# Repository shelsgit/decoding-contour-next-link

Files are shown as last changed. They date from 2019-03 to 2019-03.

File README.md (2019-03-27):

# ContourNextLink2.4/600PumpSeries - Display and Low Alarm
Instructions to make a display of your current blood sugar level with a Low Alarm and Snooze Button (for use with a Contour Next Link 2.4 and 600 series pump)<br/><br/>
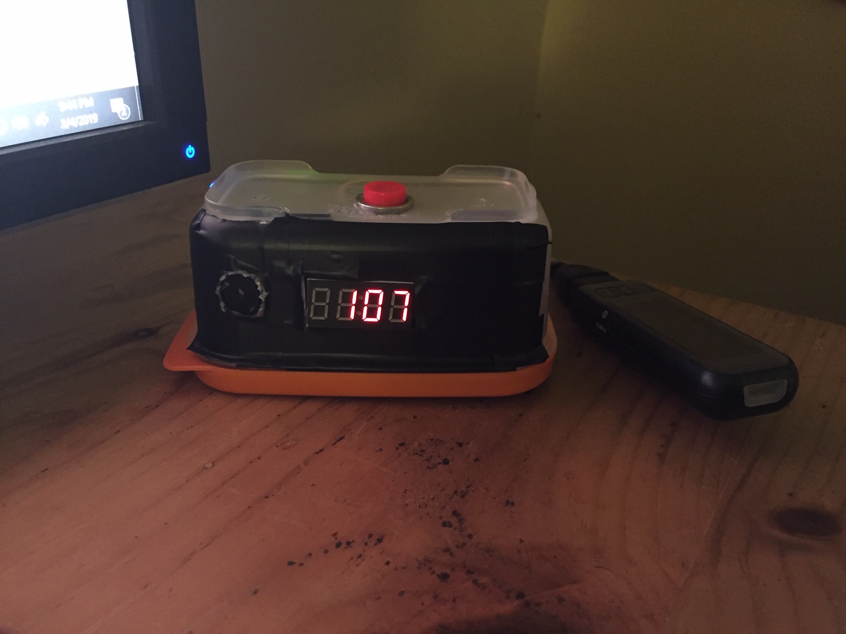
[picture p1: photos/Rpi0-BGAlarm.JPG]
BGAlarm

## Disclaimer And Warning
* All information, thought, and code described here is intended for informational and educational purposes only.<br/>
* Make/use at your own risk, and do not use the information or code to make medical decisions.<br/>
* Use of code from github.com is without warranty or formal support of any kind. Please review this repository’s LICENSE for details.<br/>
* All product and company names, trademarks, servicemarks, registered trademarks, and registered servicemarks are the property of their respective holders. Their use is for information purposes and does not imply any affiliation with or endorsement by them.<br/>
* This project has no association with and is not endorsed by Medtronic, or any other company.<br/>

## Components/Requirements
* Raspberry Pi Zero WF (RPi0)- for wifi and headless install/no miniHDMI converter needed (https://www.adafruit.com/product/3708) 
* SD/MicroSD Card (https://www.adafruit.com/product/1294)
* TM 1637 Display (https://www.amazon.com/gp/product/B01DKISMXK/ref=ppx_yo_dt_b_asin_title_o07_s00?ie=UTF8&psc=1)
* Pushbutton (https://www.amazon.com/gp/product/B01C8CS7EI/ref=ppx_yo_dt_b_asin_title_o00_s00?ie=UTF8&psc=1)
* Piezo Buzzer (https://www.adafruit.com/product/160?gclid=EAIaIQobChMIo-L8trDn4AIVyIWzCh3VjwtYEAQYASABEgKqyPD_BwE)
* Contour Next Link 2.4 (CNL) and Medtronic 600 Series Pump
* OTG cable to connect CNL to RPi0(https://www.adafruit.com/product/1099)
* Wires to connect PB and Display to RPi0 (https://www.adafruit.com/product/1950)

## RPi0 - Configure, Install Software, Start it on bootup as Service
1. Install Raspbian Lite onto your SD Card (you don't need to format or partition it prior/the install will do it):
	* Download Raspian Lite: https://www.raspberrypi.org/downloads/raspbian/
    - Note: I used 2018-10-09-raspbian-stretch (I could not headlessly configure the wireless with the later version/ not sure why - 2018-11-13-raspbian-stretch-lite)
	* Get/install Etcher (to use to move/install Raspian onto the SD card): https://www.balena.io/etcher/
	* Open etcher and flash Raspian Lite onto your SD card (Note: You don't need to format it beforehand - it will and will create a small 'boot' drive and another drive)
2. On your SD card - Edit the files below (refer to: https://learn.adafruit.com/raspberry-pi-zero-creation/text-file-editing)
	* Open file: config.txt (DONT USE NOTEPAD, Use Notepad++ or an app that won't mess up formatting):
		* At bottom add:	
		```
		# Enable UART
		enable_uart=1
		```
	* Create new file called: wpa_supplicant.conf
		* Open/edit it with your info/example below (left alligned):
		```
		ctrl_interface=DIR=/var/run/wpa_supplicant GROUP=netdev
		update_config=1
		country=US
		 
		network={
			 ssid="YOURSSID"
			 psk="YOURPASSWORD"
			 scan_ssid=1
		}
		```
	* Create a new file called ssh (no .txt extention or any extension), and don't edit it/keep it as an empty file.
3. Move the SD to the RPi0, and confirm it connects to your wireless network:
	* Eject your SD card and put it into your RPi0.  Use the 1st/TOPMOST USB PORT (if using a RPi0) and plug it into your computer - wait until green light stops blinking.
	* If you are using Windows, install Bonjour Print Services for Windows v2.0.2 - https://support.apple.com/kb/DL999?locale=en_US (I'm not sure if this is actually required but I did it)
	* Open a command prompt and try to ping the RPi0 by hostname - With windows prompt: ping raspberrypi.local
	* If you can't ping it, then you'll need to ping it by IP instead.  To figure out the RPi0's IP I have my home firewall send its event logging to: https://papertrailapp.com/.  You can setup the Rpi0 to do this as well for remote debugging, if you want.
4. SSH to the RPi0 (use PuTTY/install if you don't have):
	* Open Putty, and Enter hostname: pi@hostname(or IP) (all others default/SSH)
	* Enter default RPi0 password: raspberry
5. RPi0 Initial Setup (refer to: https://learn.adafruit.com/raspberry-pi-zero-creation/first-login)
	* Run system update:
	```
    > sudo apt-get update
    > sudo apt-get upgrade
	```
	* Run:
  	```
    > sudo raspi-config
	```
	* Select/do:
		* 'Change user password'(or similar) - change your password from default (remember it/don't loose it!)
		* 'Interfacing Options' and choose options to turn on SSH (although maybe not really needed being a boot file was made to set this on already)
		* 'Advanced Options' - Choose A1-Expand Filesystem (so that all of you SD card is available)
		* 'Update this Tool to the latest Version'

6. Install additional required Rpi0 software:
	* Confirm that you have Python 2.7 and PIP installed (Raspbian Stretch Lite comes w Python 2 and PIP for python2):
  	 ```
    > python --version
    > pip --version
	 ```
	* Install needed libraries:
	 ```
    > sudo apt-get install libusb-1.0-0-dev
    > sudo apt-get install libudev-dev
    > sudo apt-get install python-lzo
    > sudo sudo apt-get install git-core
	 ```
	* Install needed python packages:
  	 ```
    > sudo -H pip2 install cython
    > sudo -H pip2 install hidapi
    > sudo -H pip2 install requests astm PyCrypto crc16 python-dateutil
    > sudo -H pip2 install RPi.GPIO (was actually already installed)
	 ```
    - Note: If you get an error when trying any of the above installs, then read the error you get, to see which .h file or director was missing and search for a package which may include it with: apt-cache search FILENAME.  Then install it with: sudo apt-get install PACKAGENAME  
7. Git - Clone and switch to branch:
	* Clone git project:
  	 ```
    > git clone https://github.com/shelsgit/decoding-contour-next-link.git
	 ```
	* Switch to Alarm Clock Branch:
  	 ```
    > git checkout CNL-RPi0-AlarmClock
	 ```
8. Create a service to run the python clock module, at bootup:<br/>
   ** Make sure that by this step you've wired the Pushbutton and Display to the RPi0 (as in the 'Wiring' section below)  
	* Move the CNLdisplay.service file, as root to the system folder below, and then tell systemd to look for the new service:
  	 ```
    > cd /home/pi/decoding-contour-next-link/
	> sudo cp CNLdisplay.service /etc/systemd/system/CNLdisplay.service
	> sudo systemctl daemon-reload
  	 ```
	* Test it: try to start the service:
  	 ```
	> sudo systemctl start CNLdisplay.service
  	 ```
	* Check your service, to make sure its running OK:
  	 ```	
	> systemctl status CNLdisplay 
  	 ```	
	* Test it: Stop the service (and you should see 'err' on your display):
  	 ```
	> sudo systemctl stop CNLdisplay.service
	```
	* When you the service works, make it run automatically from boot up:
	```
	> sudo systemctl enable CNLdisplay.service
	```
9. Make a backup of your SD Card (optional)
	* This site looks like it has good backup/restore directions: https://www.howtogeek.com/341944/how-to-clone-your-raspberry-pi-sd-card-for-foolproof-backup/
	
## Wiring
* TM1637 Display -> RPi0 (fyi, the GPIO pin layout for a RPi0 is the same as a RPi2 or RPi3 with 40pins):
	* CLK -> GPIO23 (Pin 16, 8th pin down on right side)(top of RPi0 is when the GPIO pins are on the right)
	* DiO -> GPIO24 (Pin 18, 9th pin down on right side)
	* V -> Pi 5V Pin (Pin 2, Top pin on right side)(Could use 3V/Pin1(top,left) instead/less bright)
	* Grnd -> Pi Grnd Pin (Pin 20, 10th down on right side)
* Peizo Buzzer -> RPi0:
	* '+'-> GPIO17 (Pin 11, 6th pin down on left side)
	* Grnd -> Pi Ground Pin (Pin 9, 5th down on left side)
* Wiring Snooze Push Button -> RPi0:
	* either pushbutton terminal -> GPIO26 (left, 2nd from bottom pin)(grnd is bottom left pin)
	* other pushbutton terminal -> grnd (bottom left pin)
* Power(microUSB cable) -> RPi0:
	* microUSB -> TOP RPi0 microUSB port
* OTG cable -> RPi0:
	* OTG Cable -> 2nd (not TOP) RPi0 microUSB port

## Notes
* The Display's 1st(leftmost) digit is to display status:
	* There is a continual blinking underscore, as a heartbeat, to show that the program is running/hasn't crashed
		* The program has been very reliable for me, but if the program does crash, the display will now show 'OFF' for 20sec, then go blank, and the Rpi will be powered off.
		* If the blinking heartbeat stops for ~10s this is normal and indicates when the CNL is attempting to read from the pump (and CNL will blink yellow)
	* The 1st digit will also indicate any Recently missed, or Stale Data:
		* 0 -  the RPi0 missed one reading from the CNL (this will happen occasionally)
		* 8 - the RPi0 missed more than one reading
		* 8888 - the display data should be considered 'stale', it is ~>17min old
* The low BG setpoint = <70, and snooze time is 20min (you can change this by editing 'read_minimed_next24.py' setpoint variables near the top of the script)  
* When you turn the RPi0 on, it will take ~30sec to get your first reading (in order to give the RPi0 and meter time to startup).
* When you turn the RPi0 on, the script will run as a service, AND IT WILL STOP AND POWEROFF THE RPi0 AFTER 9 hours (this is because I want it to shutdown properly rather than pulling the power each morning, and don't want to have to SSH in each day to properly shut it down)(If you want it powered on longer or always instead, edit (then reload) your /etc/systemd/system/CNLdisplay.service)
* When the pump is calibrating or a calibration is required - the display will show 'CAL'
* The display will show 'LO' and 'HI' when the pump does.  If your display shows a value such as 776, this means something such as 'sensor updating', for example (refer to your pump, as the display will just show the big number).
* When the pump shows no signal - the display will show old then stale indication as described above (so that you can still see your previous BG and see that it is getting old and eventually stale)
* If the snooze is active and you unplug the CNL, it will buzz again when the snooze time is up until the next CNL check (when BG is not low or the data gets stale/display=8888)

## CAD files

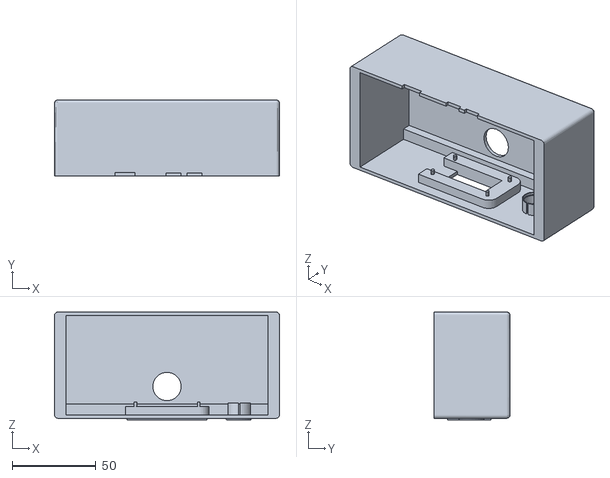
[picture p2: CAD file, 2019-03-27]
3D_Case/RPi0ClockCase1-TOP.stl
134.5 x 45.5 x 64.5

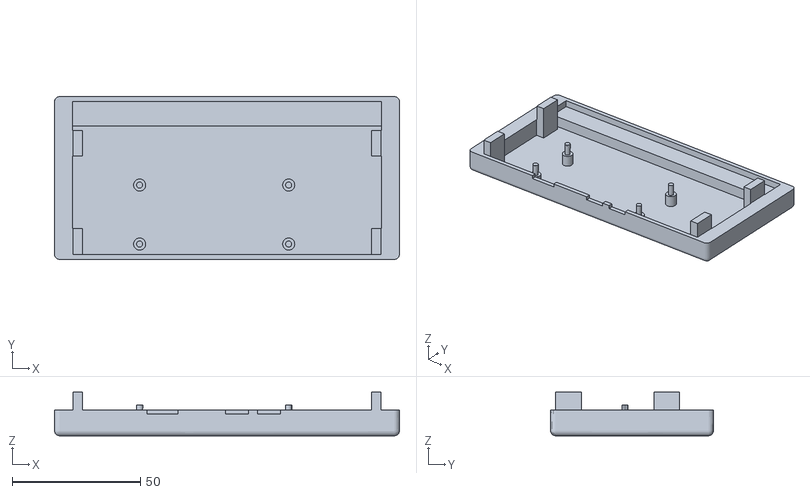
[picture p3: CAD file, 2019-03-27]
3D_Case/RPi0ClockCase1-BOTTOM.stl
134.5 x 63.5 x 17.0

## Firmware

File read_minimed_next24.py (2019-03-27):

#!/usr/bin/env python

import logging
from logging.handlers import RotatingFileHandler # Added to limit log file size
# logging.basicConfig has to be before astm import, otherwise logs don't appear
# Logging - filemode=w overrights logfile each time script is ran, .DEBUG, shows all info,warning and debug logs, .WARNING shows warning + higher, .ERROR error+)
logging.basicConfig(filename='read_mini.log',filemode='w',format='%(asctime)s %(levelname)s [%(name)s] %(message)s',level=logging.WARNING)
# a workaround on missing hidapi.dll on my windows (allows testing from saved files, but not download of pump)
try:
    import hid # pip install hidapi - Platform independant
except WindowsError:
    pass
import astm # pip install astm
import struct
import binascii
import datetime
import time
from time import sleep
import crc16 # pip install crc16
import Crypto.Cipher.AES # pip install PyCrypto
import sqlite3
import hashlib
import re
import pickle # needed for local history export
import lzo # pip install python-lzo
# from .pump_history_parser import NGPHistoryEvent, BloodGlucoseReadingEvent
from .helpers import DateTimeHelper
import tm1637 #from github-timwaizenegger/raspberrypi-examples, and copied to working dir
import RPi.GPIO as IO #also imported in tm1637, maybe I can delete from there? (did, testing)

###############################################################
# Wiring: TM1637 Display -> Raspberry Raspberry Pi Zero (RPi0) (fyi, GPIO for RPi0 is same for other RPis(2,3) that have 40pins):
# CLK -> GPIO23 (Pin 16, 8th pin down on right side of RPi0)
# DiO -> GPIO24 (Pin 18, 9th pin down on right side of RPi0)
# V -> Pi 5V Pin (Pin 2, Top pin on right side or RPi0)(Could use 3V/Pin1(top,left) instead/less bright)
# Grnd -> Pi Grnd Pin (Pin 20, 10th down on right side of RPi0)

# Wiring: Buzzer -> Rpi3:
# + -> GPIO17 (Pin 11, 6th pin down on left side of Rpi3)
# Grnd -> Pi Ground Pin (Pin 9, 5th down on right side of Rpi3)

# Wiring Snooze Push Button -> Rpi3:
# A(topleft of button) -> GPIO26 (left, 2nd from bottom pin)(grnd is bottom left pin)
# C(bottomleft of button) -> grnd (bottom left pin or Rpi3)
###############################################################

#SETPOINTS 
BGlowSP = 70 # low alarm/buzzer setpoint (mg/dL)
SnoozeTimeSP = 20 # time to snooze after snooze PB pressed (minutes)

#Define globals
realpumptime = 0
BGLtime = 0
timediff = 0
noCNL = 0
BGL = 777

logger = logging.getLogger(__name__)
handler = RotatingFileHandler("read_mini.log", maxBytes=25000, backupCount=1) # Added to limit log file size
logger.addHandler(handler) # Added to limit log file size

ascii= {
    'ACK' : 0x06,
    'CR' : 0x0D,
    'ENQ' : 0x05,
    'EOT' : 0x04,
    'ETB' : 0x17,
    'ETX' : 0x03,
    'LF' : 0x0A,
    'NAK' : 0x15,
    'STX' : 0x02
}

def ord_hack(char_or_byte):
    return char_or_byte if isinstance(char_or_byte, int) else ord(char_or_byte)

class COM_D_COMMAND:
    HIGH_SPEED_MODE_COMMAND = 0x0412
    TIME_REQUEST = 0x0403
    TIME_RESPONSE = 0x0407
    READ_PUMP_STATUS_REQUEST = 0x0112
    READ_PUMP_STATUS_RESPONSE = 0x013C
    READ_BASAL_PATTERN_REQUEST = 0x0116
    READ_BASAL_PATTERN_RESPONSE = 0x0123
    READ_BOLUS_WIZARD_CARB_RATIOS_REQUEST = 0x012B
    READ_BOLUS_WIZARD_CARB_RATIOS_RESPONSE = 0x012C
    READ_BOLUS_WIZARD_SENSITIVITY_FACTORS_REQUEST = 0x012E
    READ_BOLUS_WIZARD_SENSITIVITY_FACTORS_RESPONSE = 0x012F
    READ_BOLUS_WIZARD_BG_TARGETS_REQUEST = 0x0131
    READ_BOLUS_WIZARD_BG_TARGETS_RESPONSE = 0x0132
    DEVICE_STRING_REQUEST = 0x013A
    DEVICE_STRING_RESPONSE = 0x013B
    DEVICE_CHARACTERISTICS_REQUEST = 0x0200
    DEVICE_CHARACTERISTICS_RESPONSE = 0x0201
    READ_HISTORY_REQUEST = 0x0304
    READ_HISTORY_RESPONSE = 0x0305
    END_HISTORY_TRANSMISSION = 0x030A
    READ_HISTORY_INFO_REQUEST = 0x030C
    READ_HISTORY_INFO_RESPONSE = 0x030D
    UNMERGED_HISTORY_RESPONSE = 0x030E
    INITIATE_MULTIPACKET_TRANSFER = 0xFF00
    MULTIPACKET_SEGMENT_TRANSMISSION = 0xFF01
    MULTIPACKET_RESEND_PACKETS = 0xFF02
    ACK_MULTIPACKET_COMMAND = 0x00FE # TODO ACK_COMMAND
    NAK_COMMAND = 0x00FF
    BOLUSES_REQUEST = 0x0114
    REMOTE_BOLUS_REQUEST = 0x0100
    REQUEST_0x0124 = 0x0124
    REQUEST_0x0405 = 0x0405
    TEMP_BASAL_REQUEST = 0x0115
    SUSPEND_RESUME_REQUEST = 0x0107
    NGP_PARAMETER_REQUEST = 0x0138

class HISTORY_DATA_TYPE:
    PUMP_DATA = 0x02
    SENSOR_DATA = 0x03

class TimeoutException( Exception ):
    pass

class ChecksumException( Exception ):
    pass

class UnexpectedMessageException( Exception ):
    pass

class UnexpectedStateException( Exception ):
    pass

class NegotiationException( Exception ):
    pass

class InvalidMessageError( Exception ):
    pass

class ChecksumError( Exception ):
    pass

class DataIncompleteError( Exception ):
    pass

class Config( object ):
    def __init__( self, stickSerial ):
        self.conn = sqlite3.connect( 'read_minimed.db' )
        self.c = self.conn.cursor()
        self.c.execute( '''CREATE TABLE IF NOT EXISTS
            config ( stick_serial TEXT PRIMARY KEY, hmac TEXT, key TEXT, last_radio_channel INTEGER )''' )
        self.c.execute( "INSERT OR IGNORE INTO config VALUES ( ?, ?, ?, ? )", ( stickSerial, '', '', 0x14 ) )
        self.conn.commit()

        self.loadConfig( stickSerial )

    def loadConfig( self, stickSerial ):
        self.c.execute( 'SELECT * FROM config WHERE stick_serial = ?', ( stickSerial, ) )
        self.data = self.c.fetchone()

    @property
    def stickSerial( self ):
        return self.data[0]

    @property
    def lastRadioChannel( self ):
        return self.data[3]

    @lastRadioChannel.setter
    def lastRadioChannel( self, value ):
        self.c.execute( "UPDATE config SET last_radio_channel = ? WHERE stick_serial = ?", ( value, self.stickSerial ) )
        self.conn.commit()
        self.loadConfig( self.stickSerial )

    @property
    def hmac( self ):
        return self.data[1]

    @hmac.setter
    def hmac( self, value ):
        self.c.execute( "UPDATE config SET hmac = ? WHERE stick_serial = ?", ( value, self.stickSerial ) )
        self.conn.commit()
        self.loadConfig( self.stickSerial )

    @property
    def key( self ):
        return self.data[2]

    @key.setter
    def key( self, value ):
        self.c.execute( "UPDATE config SET key = ? WHERE stick_serial = ?", ( value, self.stickSerial ) )
        self.conn.commit()
        self.loadConfig( self.stickSerial )

class MedtronicSession( object ):
    radioChannel = None
    bayerSequenceNumber = 1
    minimedSequenceNumber = 1
    sendSequenceNumber = 0

    @property
    def HMAC( self ):
        serial = bytearray( re.sub( r"\d+-", "", self.stickSerial ), 'ascii' ) 
        paddingKey = b"A4BD6CED9A42602564F413123"
        digest = hashlib.sha256(serial + paddingKey).hexdigest()
        return "".join(reversed([digest[i:i+2] for i in range(0, len(digest), 2)]))

    @property
    def hexKey( self ):
        if self.config.key == "":
            raise Exception( "Key not found in config database. Run get_hmac_and_key.py to get populate HMAC and key." )
        return self.config.key

    @property
    def stickSerial( self ):
        return self._stickSerial

    @stickSerial.setter
    def stickSerial( self, value ):
        self._stickSerial = value
        self.config = Config( self.stickSerial )
        self.radioChannel = self.config.lastRadioChannel

    @property
    def linkMAC( self ):
        return self._linkMAC

    @linkMAC.setter
    def linkMAC( self, value ):
        self._linkMAC = value

    @property
    def pumpMAC( self ):
        return self._pumpMAC

    @pumpMAC.setter
    def pumpMAC( self, value ):
        self._pumpMAC = value

    @property
    def linkSerial( self ):
        return self.linkMAC & 0xffffff

    @property
    def pumpSerial( self ):
        return self.pumpMAC & 0xffffff

    @property
    def KEY( self ):
        return self._key

    @KEY.setter
    def KEY( self, value ):
        self._key = value

    @property
    def IV( self ):
        tmp = bytearray()
        tmp.append(self.radioChannel)
        tmp += self.KEY[1:]        
        return bytes(tmp)

class MedtronicMessage( object ):
    ENVELOPE_SIZE = 2

    def __init__( self, commandAction=None, session=None, payload=None ):
        self.commandAction = commandAction
        self.session = session
        if payload:
            self.setPayload( payload )

    def setPayload( self, payload ):
        self.payload = payload
        self.envelope = struct.pack( '<BB', self.commandAction,
            len( self.payload ) + self.ENVELOPE_SIZE )

    @classmethod
    def calculateCcitt( self, data ):
        crc = crc16.crc16xmodem( bytes(data), 0xffff )
        return crc & 0xffff

    def pad( self, x, n = 16 ):
        p = n - ( len( x ) % n )
        return x + bytes(bytearray(p))#chr(p) * p

    # Encrpytion equivalent to Java's AES/CFB/NoPadding mode
    def encrypt( self, clear ):
        cipher = Crypto.Cipher.AES.new(
            key=self.session.KEY,
            mode=Crypto.Cipher.AES.MODE_CFB,
            IV=self.session.IV,
            segment_size=128
        )

        encrypted = cipher.encrypt(self.pad(clear))[0:len(clear)]
        return encrypted

    # Decryption equivalent to Java's AES/CFB/NoPadding mode
    def decrypt( self, encrypted ):
        cipher = Crypto.Cipher.AES.new(
            key=self.session.KEY,
            mode=Crypto.Cipher.AES.MODE_CFB,
            IV=self.session.IV,
            segment_size=128
        )

        decrypted = cipher.decrypt(self.pad(encrypted))[0:len(encrypted)]
        return decrypted

    def encode( self ):
        # Increment the Minimed Sequence Number
        self.session.minimedSequenceNumber += 1
        message = self.envelope + self.payload
        crc = struct.pack( '<H', crc16.crc16xmodem( message, 0xffff ) & 0xffff )
        return message + crc

    @classmethod
    def decode( cls, message, session ):
        response = cls()
        response.session = session
        response.envelope = message[0:2]
        response.payload = message[2:-2]
        response.originalMessage = message;

        checksum = struct.unpack( '<H', message[-2:] )[0]
        calcChecksum = MedtronicMessage.calculateCcitt( response.envelope + response.payload )
        if( checksum != calcChecksum ):
            logger.info("ChecksumException.")
            raise ChecksumException( 'Expected to get {0}. Got {1}'.format( calcChecksum, checksum ) )

        return response

class ChannelNegotiateMessage( MedtronicMessage ):
    def __init__( self, session ):
        MedtronicMessage.__init__( self, 0x03, session )

        # The minimedSequenceNumber is always sent as 1 for this message,
        # even though the sequence should keep incrementing as normal
        payload = struct.pack( '<BB8s', 1, session.radioChannel,
            b'\x00\x00\x00\x07\x07\x00\x00\x02' )
        payload += struct.pack( '<Q', session.linkMAC )
        payload += struct.pack( '<Q', session.pumpMAC )

        self.setPayload( payload )
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

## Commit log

2019-03-02 Change to Display Current bloodsugar, and Alarm if low
    Changed to run on a raspberry pi zero with a display and buzzer and pushbutton - to display current bloodsugar (only) and alarm when low (and snooze PB to snooze)
    [Bayer-Medtronic-640G USB HID Interface.xlsx]
2019-03-05 wiring fix
2019-03-14 Changed CNL update time back to 15sec after pump is updated with new BGL from pump
2019-03-14 Added prints to ID CNL read issues
2019-03-15 Moved Prints, to make sure still noCNL crashes
2019-03-27 Updated README, added 3D case STL files
    [RPi0ClockCase1-BOTTOM.stl, RPi0ClockCase1-TOP.stl]
